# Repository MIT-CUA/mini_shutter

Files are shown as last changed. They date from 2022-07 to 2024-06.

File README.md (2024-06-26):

# mini_shutter and camera_shutter

## mini_shutter

Mini optical shutter using 4mm coreless DC motor and RP2040 driver using CircuitPython.  Allows a computer to control an optical shutter via a USB-C connection.

Mini-shutter in action

Mini-shutter2 in action

Uses a Waveshare <a
href="https://www.waveshare.com/rp2040-zero.htm">RP2040-Zero board</a>
and <a
href="https://learn.adafruit.com/welcome-to-circuitpython/what-is-circuitpython">Adafruit's
CircuitPython</a>.

Motor is an 0408 vibration motor, body diameter 4mm rated 3V, e.g. <a href="https://www.amazon.com/gp/product/B07PJDSRC7">this one from amazon</a>.

### Setup

Mini-shutter driver schematic:

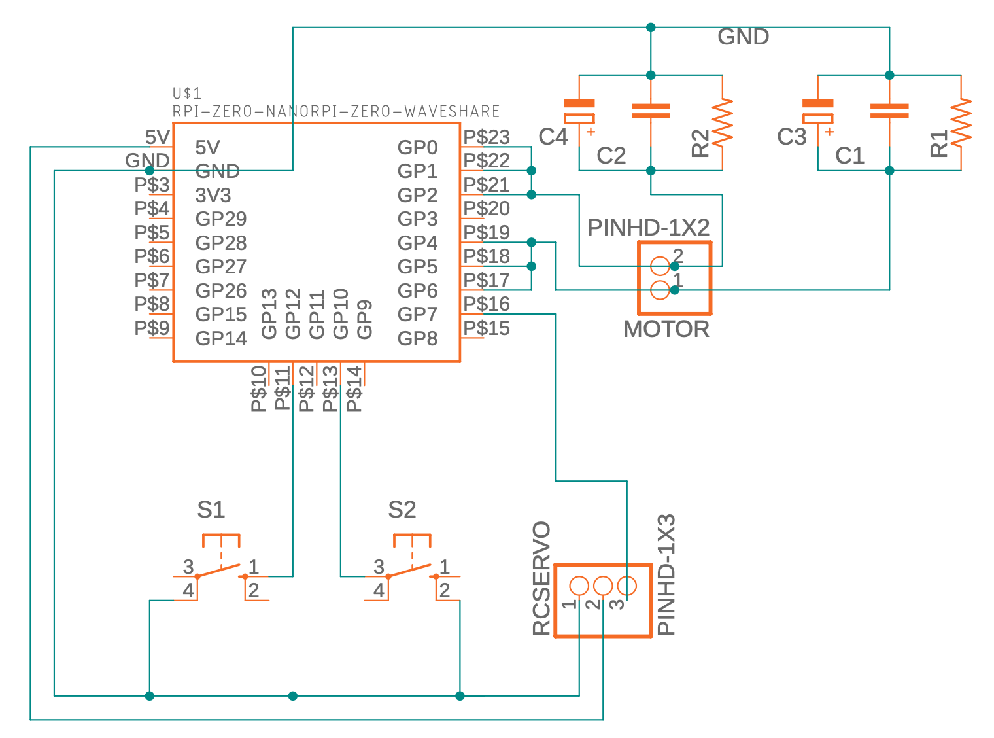
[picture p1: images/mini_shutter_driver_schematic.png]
mini-shutter driver schematic


Note that the resistors and capacitors are optional, and the header for an optional RC servo is not used.

### Loading code

1. Copy adafruit-circuitpython-raspberry_pi_pico-en_US-7.2.5.uf2 to the boot RPI-RP2 drive
2. Wait for RP2040 to re-mount itself as CIRCUITPY
3. Copy my-circuitpy-lib/* to CIRCUITPY/lib/
4. Copy mini_shutter2.py to CIRCUITPY/code.py

## camera_shutter

Camera optical shutter using DC rotating electromagnet digital camera shutter from ebay, e.g. <a href="https://www.ebay.com/itm/124456754185">this one</a>.

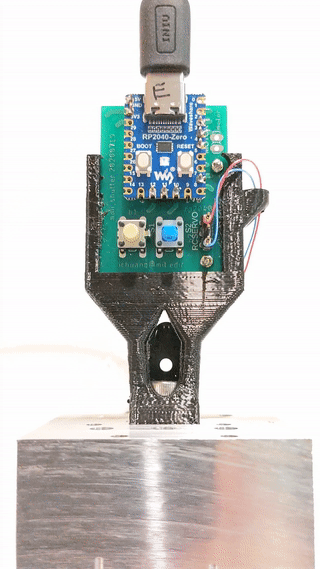
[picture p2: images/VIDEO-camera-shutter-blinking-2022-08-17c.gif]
Camera-shutter in action


Note that this shutter is normally closed, and requires a voltage to open.  The shutter springs back closed by itself when the voltage is removed.

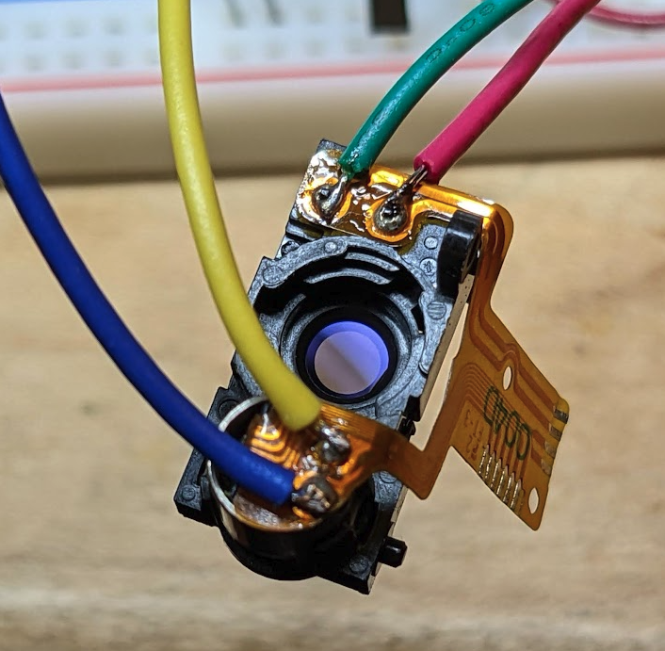
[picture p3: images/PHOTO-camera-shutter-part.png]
camera shutter part


Also, the camera shutter module has another solenoid which moves some kind of filter (or polarizer) into (and out of) the beam path, when energized (or energized in the reverse direction).

## code

See [camera_shutter.py](camera_shutter.py). New code in [main.py](ndsp/main.py), [shutter.py](ndsp/shutter.py), [photodiode.py](ndsp/photodiode.py), and [boot.py](ndsp/boot.py).

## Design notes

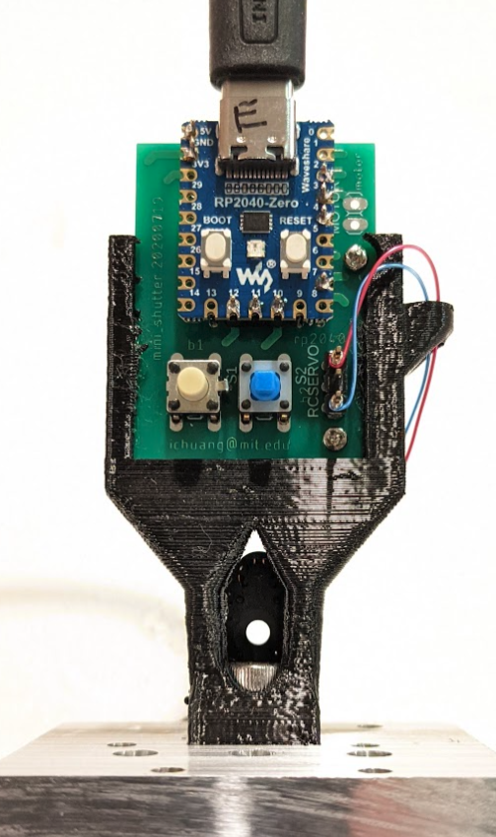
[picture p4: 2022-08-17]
images/PHOTO-camera-shutter-rp2040.png

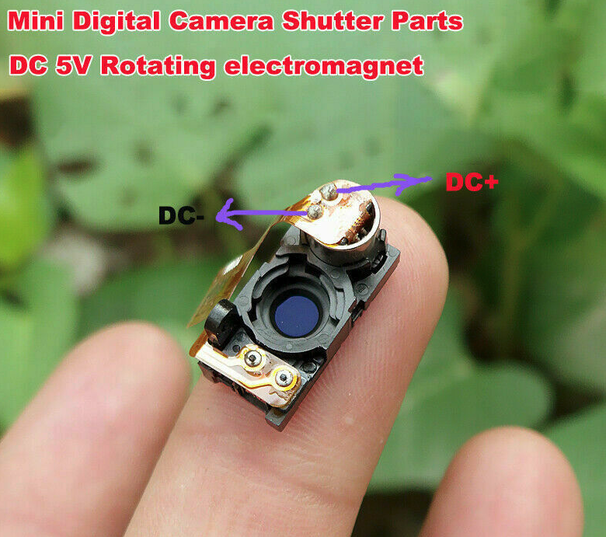
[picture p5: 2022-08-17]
images/IMAGE-digital-camera-shutter-micro-rotating-electromagnet-from-ebay-2022-08-07.png

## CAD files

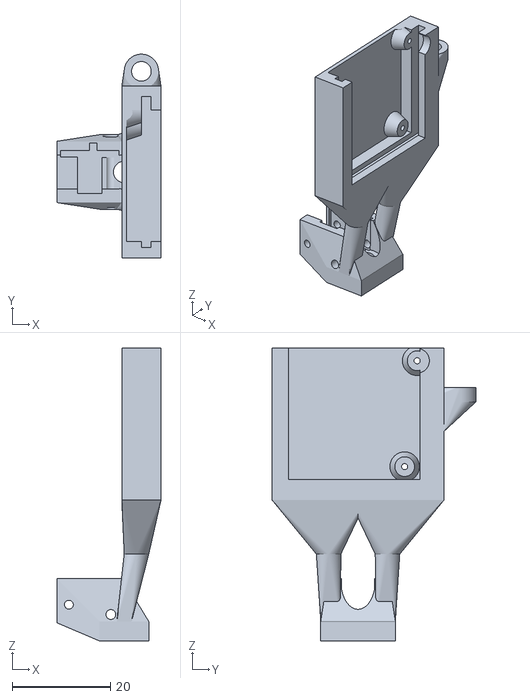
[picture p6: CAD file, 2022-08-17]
camera_shutter_mount_with_elec.stl
21.2 x 41.5 x 59.7

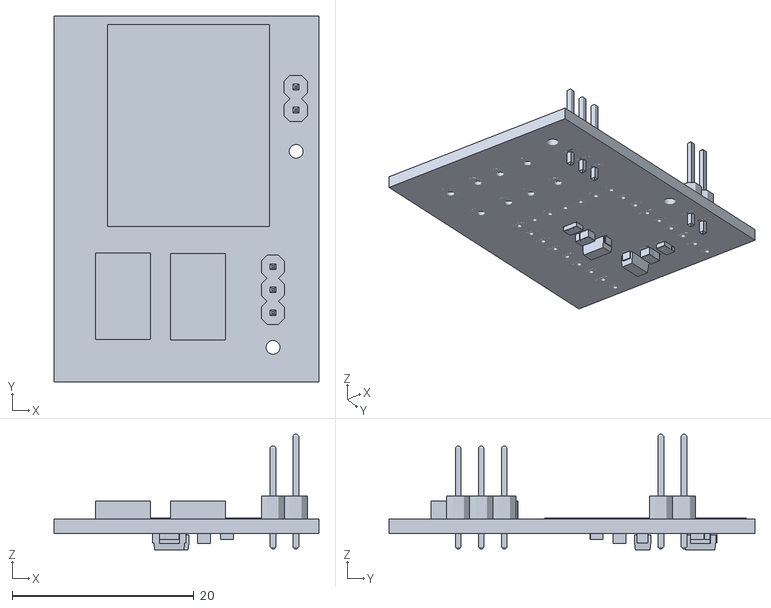
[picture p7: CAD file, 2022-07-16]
electronics/mini_shutter_driver v1.stl
29.2 x 40.3 x 12.7

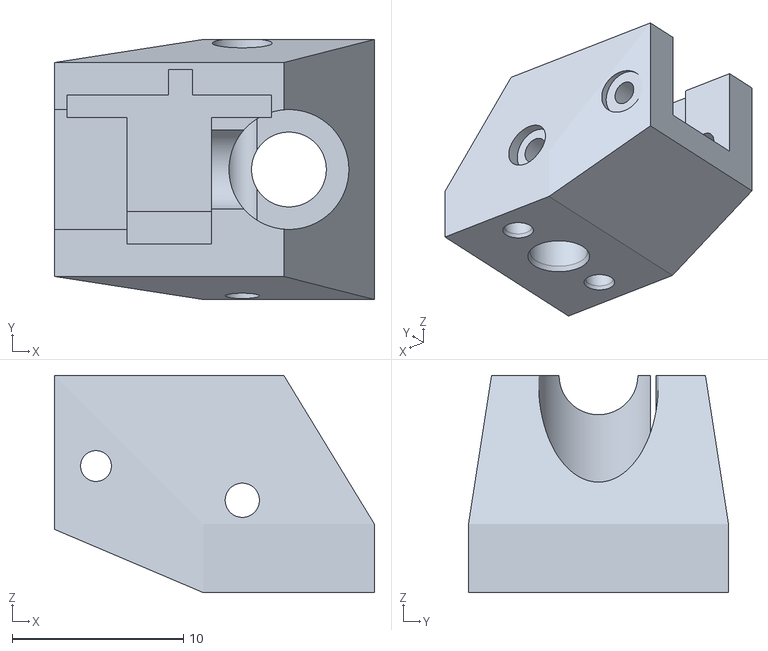
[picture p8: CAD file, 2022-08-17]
camera_shutter_mount.stl
18.7 x 15.2 x 12.7

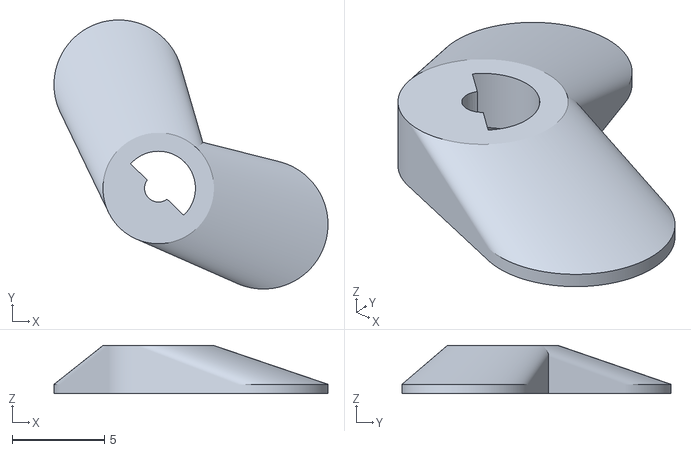
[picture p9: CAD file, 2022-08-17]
mini_shutter_blade_balanced.stl
14.8 x 14.6 x 2.60

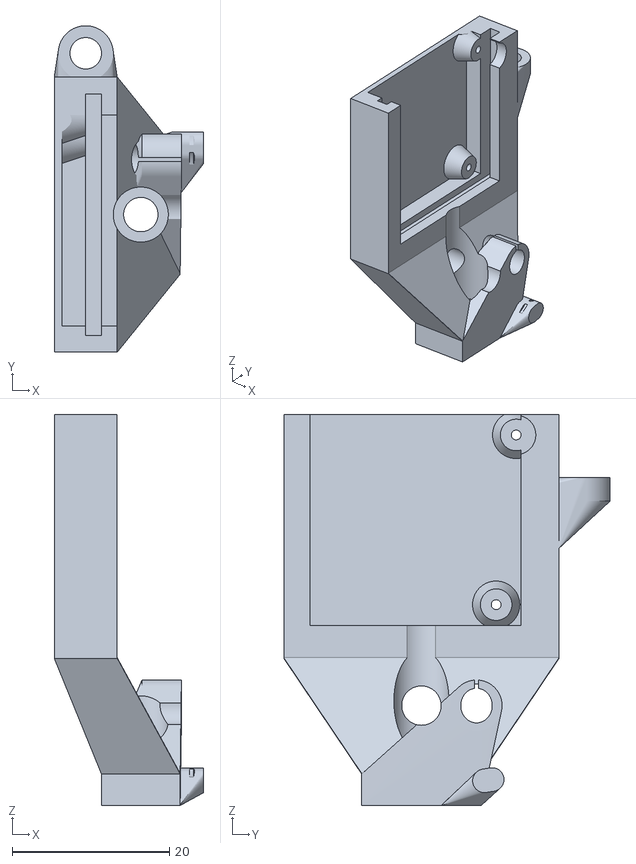
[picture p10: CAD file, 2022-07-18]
mini_shutter_mount.stl
19.0 x 41.5 x 49.7

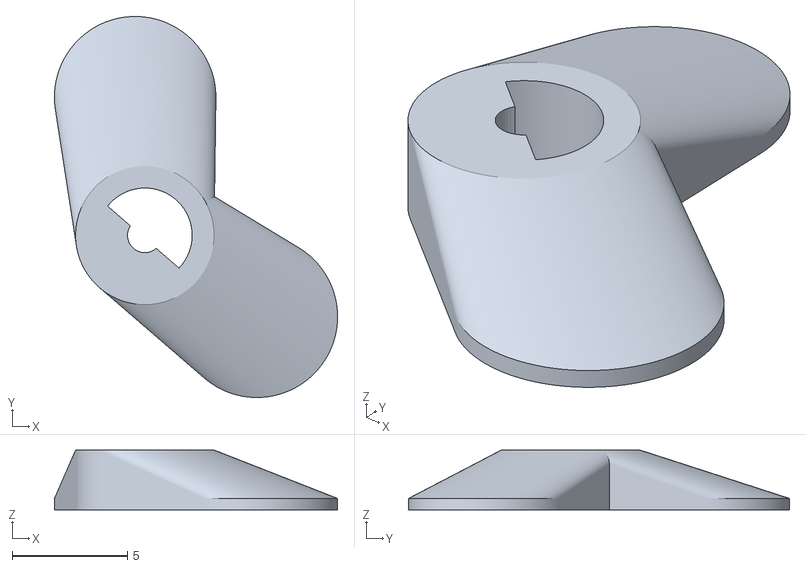
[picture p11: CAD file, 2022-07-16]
mini_shutter_blade.stl
12.3 x 16.5 x 2.60

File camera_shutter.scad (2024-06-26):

//
// camera shutter used as an optical shutter
//

//-----------------------------------------------------------------------------
// global constants

use<util.scad>;

d_inch = 25.4;
pi = 3.14159;

$fa = 0.5; // default minimum facet angle is now 0.5
$fs = 0.1; // default minimum facet size is now 0.5 mm

screw_clear_dia_4_40 = 0.120 * d_inch;
screw_tap_dia_4_40 = 0.089 * d_inch;
screw_nut_dia_4_40 = 6.4;
screw_head_clear_dia_4_40 = 5.50; // actually, pan screw head

screw_clear_dia_6_32 = 0.1450 * d_inch;
screw_tap_dia_6_32 = 0.1065 * d_inch;
screw_nut_dia_6_32 = 7.9;

screw_clear_dia_8_32 = 0.172 * d_inch;
screw_tap_dia_8_32 = 0.1360 * d_inch;
screw_nut_dia_8_32 = 8.7;           // measured from flat to flat
screw_head_clear_dia_8_32 = 7.00;   // hex
screw_washer_clear_dia_8_32 = 9.70; // thorlabs 8-32 kit washer
screw_self_tap_dia_8_32 = screw_tap_dia_8_32 + 0.5; // self-tapping for 8-32

pcb_global_z_offset = -5.0;

//-----------------------------------------------------------------------------
// camera shutter model

module cots_dc5v_camera_shutter(show = true, drill = false) {
    //
    // Uses "DC 5V Digital Camera Shutter Micro Rotating electromagnet Control
    // Switch" from ebay:
    // https://www.ebay.com/itm/124456754185?hash=item1cfa335c09:g:8tIAAOSwq4Nh7qDp
    //
    // oriented with shutter in yz plane, optical axis along x, magnet housing
    // pointing to +x and sitting above shutter.
    //
    // origin in middle of aperture
    //
    cs_dy = 8.5 + (drill ? 0.2 : 0);
    cs_dz = 17.9;
    cs_magnet_dx = 8.6;
    cs_magnet_zoff = 15.5;
    cs_magnet_dia = 6.2;
    cs_bot_stub_dy = 1.5 + (drill ? 0.4 : 0);
    cs_bot_stub_dz = 0.7 + (drill ? 0.2 : 0);
    cs_bot_dx = 4.65; // includes leads to electromagnet on bottom
    cs_dx = 4.75;     // midpoint including funnel to aperture
    // cs_aperture_dia = 6.36;
    cs_aperture_dia = 4.5;
    cs_aperture_zpos = 8.8; // distance from bottom (above stub)
    cs_bot_strut_hole_dia = 1.5 + (drill ? 0.5 : 0);
    cs_bot_strut_dx = 3.4;                      // length from back surface
    cs_bot_strut_dy = 1.2 + (drill ? 0.17 : 0); // thickness
    cs_bot_strut_dz = 3.0;
    cs_bot_strut_hole_zpos = (cs_bot_strut_dz - cs_bot_strut_hole_dia) / 2 +
                             cs_bot_strut_hole_dia / 2;
    cs_bot_strut_hole_xpos =
        -cs_dx / 2 - cs_bot_strut_dx + cs_bot_strut_hole_zpos;

    bot_pin_dz = 1.2;
    bot_pin_dx = 1.2 + (drill ? 0.3 : 0);
    bot_pin_dy = 1.5 + (drill ? 0.1 : 0);
    bot_pin_zoff = 2.8 - bot_pin_dz;
    bot_pin_xoff = 2.3 - bot_pin_dx + (drill ? 0.15 : 0);

    up_strut_dx = 3.4;
    up_strut_dy = 1.2 + (drill ? 0.1 : 0);
    up_strut_dz = 3.0;
    up_strut_hole_dia = 1.5 + (drill ? 0.3 : 0);
    up_strut_zpos = 5 - up_strut_dz;
    up_strut_hole_zpos = up_strut_zpos + up_strut_dz / 2;
    up_strut_hole_xpos = cs_dx / 2 + up_strut_dx - up_strut_dz / 2;

    cut_bot_strut_dx = cs_bot_strut_dx + (drill ? 0.2 : 0);
    cut_up_strut_dx = up_strut_dx + (drill ? 0.2 : 0);

    screw_clear_head_dia_1_7mm = 3.1 + 0.4; // head diameter for 1.7mm screw

    bot_mag_cut_dx = 20;
    bot_mag_cut_dz = 20;
    bot_mag_cut_dy = 7;
    bot_mag_cut_zoff = 2;

    bot_front_cut_dx = 6;

    module holes() {
        screw_head_yoff = cs_dy / 2 + 2;
        color("red") {
            translate([ 0, 0, cs_aperture_zpos ]) rotate([ 0, 90, 0 ])
                translate([ 0, 0, -10 ])
                    cylinder(d = cs_aperture_dia,
                             h = 20); // main aperture for optical beam path
            translate([ cs_bot_strut_hole_xpos, 0, cs_bot_strut_hole_zpos ]) {
                rotate([ 90, 0, 0 ]) {
                    translate([ 0, 0, -10 ]) cylinder(
                        d = cs_bot_strut_hole_dia, h = 20); // bottom strut hole
                    translate([ 0, 0, screw_head_yoff ]) cylinder(
                        d = screw_clear_head_dia_1_7mm, h = 20); // screw head
                }
            }
            translate([ up_strut_hole_xpos, 0, up_strut_hole_zpos ]) {
                rotate([ 90, 0, 0 ]) {
                    translate([ 0, 0, -10 ]) cylinder(d = up_strut_hole_dia,
                                                      h = 20); // up strut hole
                    translate([ 0, 0, screw_head_yoff ]) cylinder(
                        d = screw_clear_head_dia_1_7mm, h = 20); // screw head
                }
            }
        }
    }

    translate([ 0, 0, -cs_aperture_zpos ]) {
        difference() {
            union() {
                cut_dx = cs_dx + (drill ? 0.2 : 0);
                color("silver") translate([ -cut_dx / 2, -cs_dy / 2, 0 ])
                    cube([ cut_dx, cs_dy, cs_dz ]);
                color("gray") translate([
                    -cut_dx / 2, -cs_bot_stub_dy + cs_dy / 2,
                    -cs_bot_stub_dz + 0.01
                ]) // stub on bottom right
                    cube([ cut_dx, cs_bot_stub_dy, cs_bot_stub_dz ]);
                color("black") translate([
                    -cut_bot_strut_dx - cs_dx / 2, -cs_dy / 2, 0
                ]) // strut bottom left back
                    cube(
                        [ cut_bot_strut_dx, cs_bot_strut_dy, cs_bot_strut_dz ]);
                color("black") translate([
                    cs_dx / 2, -cs_dy / 2,
                    up_strut_zpos
                ]) // strut upper left front
                    cube([ cut_up_strut_dx, up_strut_dy, up_strut_dz ]);
                color("black") translate([
                    -cs_dx / 2 + bot_pin_xoff, -cs_dy / 2 - bot_pin_dy,
                    bot_pin_zoff
                ]) // bottom pin
                    cube([ bot_pin_dx, bot_pin_dy, bot_pin_dz ]);
                color("green") translate(
                    [ -cs_dx / 2, 0, cs_magnet_zoff ]) // magnet cylinder
                    rotate([ 0, 90, 0 ])
                        cylinder(d = cs_magnet_dia, h = cs_magnet_dx);
            }
            holes();
        }
        if (drill) {
            color("pink") {
                translate([ cs_dx / 2, -cs_dy / 2, 0 ]) // slot for up strut
                    cube([ cut_up_strut_dx, up_strut_dy, up_strut_zpos + 14 ]);
                translate([
                    -cut_bot_strut_dx - cs_dx / 2, -cs_dy / 2, 0
                ]) // slot for bot strut
                    cube([
                        cut_bot_strut_dx, cs_bot_strut_dy, cs_bot_strut_dz + 10
                    ]);
                translate([
                    -cs_dx / 2 + bot_pin_xoff, -cs_dy / 2 - bot_pin_dy + 0.01, 0
                ]) // bottom pin
                    cube([ bot_pin_dx, bot_pin_dy, 16 ]);
                translate([
                    -cs_dx / 2, -bot_mag_cut_dy / 2,
                    bot_mag_cut_zoff
                ]) // cutout to access bottom magnet pins
                    cube([ bot_mag_cut_dx, bot_mag_cut_dy, bot_mag_cut_dz ]);
                translate([
                    -bot_front_cut_dx, -bot_mag_cut_dy / 2,
                    bot_mag_cut_zoff
                ]) // cutout for bottom front
                    cube([ bot_front_cut_dx, bot_mag_cut_dy, bot_mag_cut_dz ]);
            }
            holes();
        }
    }
}

// -----------------------------------------------------------------------------
// c05g mount onto baseplate

module baseplate_mount_holes(slen = 5) {
    //
    // holes for mounting onto baseplate: 8-32 screw and two 2mm pins,
    // compatible with footprint of thorlabs c05 polaris mirror mount.
    //
    // slen = screw length (dz before screw head)
    //
    pin_dia = 2.0;
    pin_dy = 5.0;
    pin_dz = 2.2;
    cylinder(d = screw_clear_dia_8_32, h = 20 - 6);
    translate([ 0, 0, slen ]) {
        cylinder(d = screw_head_clear_dia_8_32, h = 20 - 8);
    }
    translate([ 0, 0, -0.01 ])
        cylinder(d1 = screw_clear_dia_8_32 + 0.4, d2 = screw_clear_dia_8_32,
                 h = 0.5); // taper to compensate for print bed lip
    for (dy = [ -1, 1 ]) {
        translate([ 0, dy * pin_dy, 0 ]) {
            cylinder(d = pin_dia + 0.1, h = pin_dz);
            translate([ 0, 0, -0.01 ])
                cylinder(d1 = pin_dia + 0.4, d2 = pin_dia + 0.1,
                         h = 0.4); // taper to compensate for print bed lip
        }
    }
}

// -----------------------------------------------------------------------------
// controller electronics

module controller_pcb(show = true, drill = false, holes = false) {
    // PCB in XY plane with origin on bottom side at y-midpoint along board edge
    // pointing along -x direction
    pcb_dx = 29.2;
    pcb_dy = 40.35;
    pcb_thick = 2;

    mount_screw_dia = 1.25;
    mount_screw_head_dia = 5;

    if (show) {
        rotate([ 0, 0, 90 ]) translate([ -pcb_dx / 2, -pcb_dy * 0, 0 ])
            import("electronics/mini_shutter_driver v1.stl");
    }
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

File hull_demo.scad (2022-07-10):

// illustrate use of hull() for connecting parts

$fa=0.5; // default minimum facet angle is now 0.5
$fs=0.1; // default minimum facet size is now 0.1 mm

module first(){
     color("orange") cube([10, 10, 4]);
     color("blue") translate([0, 0, 8]) rotate([0, 90, 0])
	  cylinder(d=4, h=8);
}

module second(){
     color("orange"){

	  hull(){
	       cube([10, 10, 4]);
	       translate([0, 0, 8]) rotate([0, 90, 0])
		    cylinder(d=4, h=8);
	  }

     }
}

module third(){
     color("blue")
	  translate([0, 0, 8]) rotate([0, 90, 0]) cylinder(d=3, h=12);
     color("orange"){
	  hull(){
	       cube([10, 10, 4]);
	       translate([2, 0, 8]) rotate([0, 90, 0])
		    cylinder(d=4, h=4);
	  }
     }
}

// first();
second();
// third();

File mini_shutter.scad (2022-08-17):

//
// mini optical shutter for baseplate (1/2" beam height) using
// 4mm diameter coreless DC motor.
//
// motor is easily driven by current from digital output pin
// of RP2040 microcontroller

//-----------------------------------------------------------------------------
// global constants

use <util.scad>;

d_inch = 25.4;
pi = 3.14159;

$fa=0.5; // default minimum facet angle is now 0.5
$fs=0.1; // default minimum facet size is now 0.5 mm

screw_clear_dia_4_40 = 0.120 * d_inch;
screw_tap_dia_4_40   = 0.089 * d_inch;
screw_nut_dia_4_40   = 6.4;
screw_head_clear_dia_4_40 = 5.50;	// actually, pan screw head

screw_clear_dia_6_32 = 0.1450 * d_inch;
screw_tap_dia_6_32   = 0.1065 * d_inch;
screw_nut_dia_6_32   = 7.9;

screw_clear_dia_8_32 = 0.172 * d_inch;
screw_tap_dia_8_32   = 0.1360 * d_inch;
screw_nut_dia_8_32   = 8.7;		// measured from flat to flat
screw_head_clear_dia_8_32 = 7.00;	// hex
screw_washer_clear_dia_8_32 = 9.70;	// thorlabs 8-32 kit washer
screw_self_tap_dia_8_32 = screw_tap_dia_8_32 + 0.5;		// self-tapping for 8-32

// -----------------------------------------------------------------------------
// options


// -----------------------------------------------------------------------------
// mini 4mm coreless dc motor

module motor_4mm_coreless_dc(show=true, drill=false, theta=-45, drill_slot=true, mount_dia_extra=0){
     //
     // motor pointing up towards +z, positioned with bottom of cam
     // (closest side of cam to motor) at origin.  shaft has a cam on it.
     //
     // theta = angle of motor cam
     // drill_slot = include slot for motor housing clamp
     // 
     body_dz = 8.2;
     shaft_dia = 0.75;
     cam_outer_dia = 4.0;
     cam_dz = 2.5;
     cam_shaft_dia = 1.5;
     cam_yoff = -0.1;
     oal = 11.4;				// overall length
     slot_dy = 0.5;
     slot_dx = 8;
     module cam(show=true, drill=false){
	  color("blue"){
	       acod = cam_outer_dia + (drill ? 0.9 - 0.9 : 0);
	       rotate([-50, 0, 0])
		    translate([-acod/2, -0.4 + cam_yoff, -0.3]){	// compensate for print burr - flat side
			 color("red") cube([acod, 0.5, 0.7]);
		    }
	       cylinder(d=cam_shaft_dia, h=cam_dz + (drill ? 1 : 0) );	// cam center - on shaft
	       cylinder(d1=cam_shaft_dia + (drill ? 0.9 + 0.4 : 0), d2=cam_shaft_dia, h=0.6 );	// cam center - on shaft - compensate for print plate burr
	       difference(){
		    union(){
			 cylinder(d1=cam_outer_dia + (drill ? 0.9 + 0.2 : 0),	// compensate for burr on print plate
				  d2=cam_outer_dia + (drill ? 0.0 : 0),
				  h=0.6);
			 cylinder(d=cam_outer_dia + (drill ? 0.0 : 0),
				  h=cam_dz + (drill ? 1 : 0));
		    }
		    translate([-5, -10 + cam_yoff, -1]){
			 color("red") cube([10, 10, 10]);
		    }
	       }
	  }
     }
     union(){
	  extra_dz = (drill ? 8 : 0);		// extra tube length when drilling, for wires to exit
	  extra_dia = mount_dia_extra;		// possibly different diameter when drilling, so motor fits snugly in motor housing
	  translate([0, 0, -oal + cam_dz]){
	       translate([0, 0, -extra_dz]) color("silver"){
		    scale([1 + (drill ? 0.1 : 0), 1, 1])	// for holder, compensate for underhang from top when printing
			 cylinder(d=4 + extra_dia, h=body_dz + extra_dz);	// main cylindrical body of motor
		    if (drill && drill_slot){
			 // cut slot along side of motor, so the motor housing can hold motor with natural spring clamp action
			 translate([-slot_dx, -slot_dy/2, 0])
			      cube([slot_dx, slot_dy, body_dz + extra_dz]);
		    }
	       }
	       translate([0, 0, 0.01]) color("black") cylinder(d=cam_shaft_dia, h=oal-0.01);	// motor shaft
	  }
	  rotate([0, 0, theta])
	       cam(show=show, drill=drill);		// cam at end of shaft
     }
}

// -----------------------------------------------------------------------------
// c05g mount onto baseplate

module baseplate_mount_holes(slen=5){
     //
     // holes for mounting onto baseplate: 8-32 screw and two 2mm pins,
     // compatible with footprint of thorlabs c05 polaris mirror mount.
     //
     // slen = screw length (dz before screw head)
     //
     pin_dia = 2.0;
     pin_dy = 5.0;
     pin_dz = 2.2;
     cylinder(d=screw_clear_dia_8_32, h=20);
     translate([0, 0, slen]){
	  cylinder(d=screw_head_clear_dia_8_32, h=20);
     }
     translate([0, 0, -0.01])
	  cylinder(d1=screw_clear_dia_8_32 + 0.4, d2=screw_clear_dia_8_32, h=0.5);	// taper to compensate for print bed lip
     for(dy=[-1,1]){
	  translate([0, dy*pin_dy, 0]){
	       cylinder(d=pin_dia+0.1, h=pin_dz);
	       translate([0, 0, -0.01])
		    cylinder(d1=pin_dia + 0.4, d2=pin_dia + 0.1, h=0.4);	// taper to compensate for print bed lip
	  }
     }
}

// -----------------------------------------------------------------------------
// controller electronics

module controller_pcb(show=true, drill=false, holes=false){
     // PCB in XY plane with origin on bottom side at y-midpoint along board edge
     // pointing along -x direction
     pcb_dx = 29.2;
     pcb_dy = 40.35;
     pcb_thick = 2;

     mount_screw_dia = 1.25;
     mount_screw_head_dia = 5;

     if (show){
	  rotate([0, 0, 90])
	       translate([-pcb_dx/2, -pcb_dy*0, 0])
	       import("electronics/mini_shutter_driver v1.stl");
     }

     module mounting_holes(zoff=0){
	  for(xy=[ [-3.83, 9.5], [-25.4, 9.5+2.54] ]){
	       translate([xy[0], xy[1], zoff])
		    children();
	       }
     }

     if (drill){
	  if (1){
	       slot_width = pcb_dx + 1.5;
	       translate([ -pcb_dy, -slot_width/2, 0]){
		    color("pink"){
			 cube([pcb_dy, slot_width, pcb_thick]);			// PCB
		    }
		    color("orange"){					// components on PCB
			 rim = 1.2;
			 comp_thick = 7;
			 translate([-rim, rim, -0.01])
			      cube([pcb_dy, pcb_dx-2*rim, comp_thick]);		// top-side components
		    }
		    difference(){
			 color("brown"){					// bottom-side components on PCB
			      rim = 1.2;
			      comp_thick = 3;
			      translate([-rim, rim, -comp_thick])
				   cube([pcb_dy, pcb_dx-2*rim, comp_thick]);		// bottom-side components
			 }
			 color("red"){
			      translate([ pcb_dy, slot_width/2, -3]){
				   mounting_holes(){
					cylinder(d1=6, d2=4, h=3);		// feet for mounting screws
				   }
			      }
			 }
		    }
	       }
	  }
	  color("red"){
	       mounting_holes(zoff=-10)
		    cylinder(d=mount_screw_dia, h=20);		// screw holes
	       mounting_holes(zoff=0)
		    cylinder(d=mount_screw_head_dia, h=20);		// screw head holes
	  }
     }

     if (holes){
	  mounting_holes();
     }
}

module electronics_mount(show=true, show_bottom=false, show_electronics=false){
     //
     // mount for control electronics PCB, oriented in lab frame (of final optical shutter).
     // holds PCB from outer rim, to allow space for components (on both sides of PCB),
     // including the RP2040 module.
     // Open at top for USB-C connector
     // Open at front for push-buttons
     //
     // if show_bottom then make rectangle for bottom of mount (for hull to something else)
     //
     mount_dy = 35;
     mount_dx = 8;
     mount_dz = 40 - 9;
     mount_xoff = -2;
     pcb_zoff = 3;

     module epos(){
	  translate([0, 0, pcb_zoff])
	       rotate([0, 90, 0])
	       children();
     }

     module bottom(){
	  translate([-mount_dx/2, -mount_dy/2, 0])
	       cube([mount_dx, mount_dy, 0.1]);
     }

     if (show){
	  difference(){
	       sr_zoff = 24 - 4;	// strain relief z-offset
	       sr_yoff = 3;
	       sr_od = mount_dx-1;
	       sr_id = 4;
	       sr_dz = 3;
	       union(){
		    translate([-mount_dx/2, -mount_dy/2, 0])
			 color("blue")
			 cube([mount_dx, mount_dy, mount_dz]);
		    difference(){
			 hull(){
			      translate([0, mount_dy/2 + sr_yoff, sr_zoff])
				   cylinder(d=sr_od, h=sr_dz);
			      translate([0, 0, sr_zoff-sr_dz - 3])
				   bottom();
			 }
			 translate([0, mount_dy/2 + sr_yoff, sr_zoff-10])
			      color("red")
			      cylinder(d=sr_id, h=20);
		    }
	       }
	       epos()
		    controller_pcb(show=false, drill=true);
	  }
     }
     if (show_bottom){
	  bottom();
     }
     if (show_electronics){
	  epos()
	       controller_pcb(show=true, drill=false);
     }
}

// -----------------------------------------------------------------------------
// shutter with mount
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

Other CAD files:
util.scad

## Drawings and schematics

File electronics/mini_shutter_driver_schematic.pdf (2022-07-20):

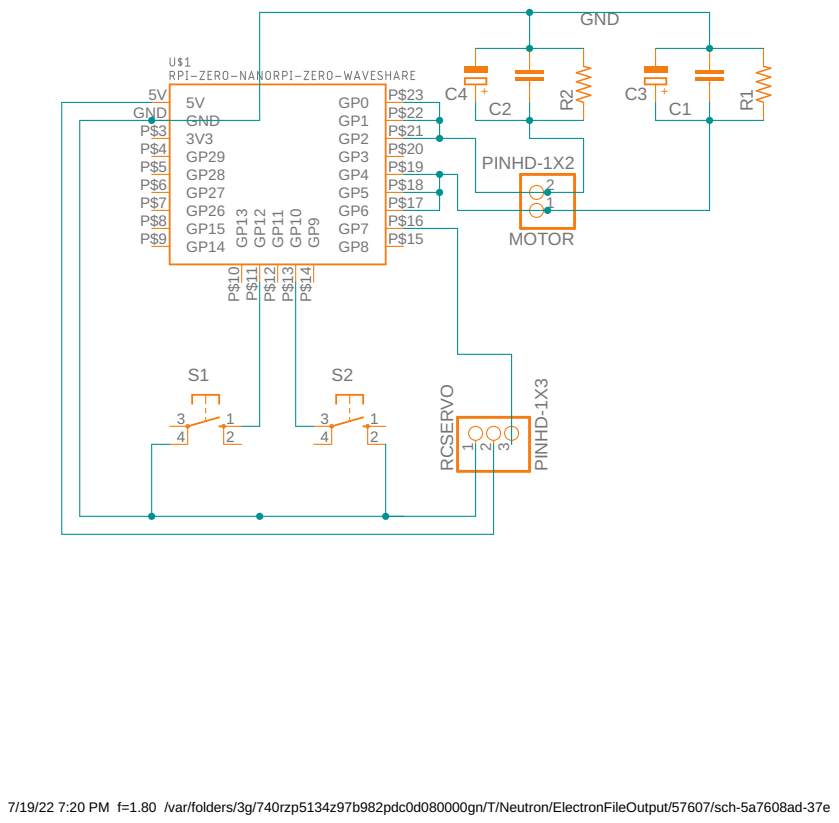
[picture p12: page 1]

7/19/22 7:20 PM f=1.80 /var/folders/3g/740rzp5134z97b982pdc0d080000gn/T/Neutron/ElectronFileOutput/57607/sch-5a7608ad-37e2-4f54-81ba-9fdea8c5b5c8/Untitled.sch (Sheet: 1/1)

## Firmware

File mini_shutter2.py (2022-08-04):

#
# mini_shutter2.py: run 4mm coreless DC motor (used for an optical shutter)
# either back and forth - opening and closing repeatedly
# or button pushes to open & close
#

import time
import board
import pwmio
import usb_hid
import neopixel
import supervisor
from digitalio import DigitalInOut, Direction, Pull
from adafruit_debouncer import Debouncer

# BUTTON_PIN = board.GP27
BUTTON_PIN = board.GP12
the_button = DigitalInOut(BUTTON_PIN)		# button digital input
the_button.direction = Direction.INPUT
the_button.pull = Pull.UP

# BUTTON_PIN2 = board.GP15
BUTTON_PIN2 = board.GP10
the_button2 = DigitalInOut(BUTTON_PIN2)		# button digital input
the_button2.direction = Direction.INPUT
the_button2.pull = Pull.UP

# motor_open = DigitalInOut(board.GP7)
# motor_close = DigitalInOut(board.GP6)

motor_open_pins  = [ board.GP0, board.GP1, board.GP2 ]
motor_close_pins = [ board.GP4, board.GP5, board.GP6 ]
motor_open  = [ pwmio.PWMOut(m, frequency=500, duty_cycle=0) for m in motor_open_pins ]
motor_close = [ pwmio.PWMOut(m, frequency=500, duty_cycle=0) for m in motor_close_pins ]

sw1 = Debouncer(the_button)
sw2 = Debouncer(the_button2)

led = neopixel.NeoPixel(board.GP16, 1)
led.brightness = 0.3

print("mini_shutter2.py")
print("(h) help")

def shutter_open():
    led[0] = (5, 0, 0)
    for m in motor_close:
        m.duty_cycle = 0
    for cycle in range(32768, 65535, 1000):
        for m in motor_open:
            m.duty_cycle = cycle
    time.sleep(0.3)
    for m in motor_open:
        # m.duty_cycle = 10000	# keep slightly powered
        m.duty_cycle = 0	# unpowered
    led[0] = (0, 0, 0)
    print("open")
    
def shutter_close():
    led[0] = (0, 5, 0)
    for m in motor_open:
        m.duty_cycle = 0
    for cycle in range(32768, 65535, 1000):
        for m in motor_close:
            m.duty_cycle = cycle
    time.sleep(0.3)
    for m in motor_close:
        m.duty_cycle = 0
    led[0] = (0, 0, 0)
    print("close")

def process_buttons():
    global mode
    sw1.update()		# button debouncing
    sw2.update()
    if not sw1.value:
        shutter_open()
        while not sw1.value:    # Wait for button to be released
            if not sw2.value:	# if both buttons pushed
                mode = "osc"
            sw1.update()
            sw2.update()
        return
        
    if not sw2.value:
        shutter_close()
        while not sw2.value:    # Wait for button to be released
            if not sw1.value:	# if both buttons pushed
                mode = ""
            sw1.update()
            sw2.update()
        return

mode = ""
opened = False
last_time = time.monotonic()

def oscillate():
    global opened, last_time
    now = time.monotonic()
    if now-last_time < 0.5:
        return
    last_time = now
    if opened:
        shutter_close()
        opened = False
    else:
        shutter_open()
        opened = True

def process_input():
    global mode
    if not supervisor.runtime.serial_bytes_available:
        return
    value = input().strip()
    if value=="r":
        print("running oscillation...")
        mode = "osc"
    elif value=="o":
        mode = ""
        shutter_open()
    elif value=="c":
        mode = ""
        shutter_close()
    elif value=="s":
        mode = ""
        print("stopped")
    elif value=="h":
        print("(o) open, (c) close, (r) run oscillate, (s) stop")

# flicker LED to indicate power-up
led[0] = (5, 0, 0)
time.sleep(0.1)
led[0] = (0, 5, 0)
time.sleep(0.1)
led[0] = (0, 0, 5)
time.sleep(0.1)
led[0] = (0, 0, 0)
shutter_open()

# main loop
while True:
    process_buttons()
    process_input()
    if mode=="osc":
        oscillate()

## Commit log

2022-07-10 mini_shutter OpenSCAD and circuitpython code
    [mini_shutter.scad, mini_shutter_blade.stl, mini_shutter_mount.stl]
2022-07-10 mini_shutter.scad - better endstop latching for closed position
    [mini_shutter.scad, mini_shutter_mount.stl]
2022-07-10 add hull_demo.scad
    [hull_demo.scad]
2022-07-15 change motor pins to match pcb
2022-07-16 mini shutter scad with mount for control electronics - also larger blade block and movement
    [mini_shutter.scad, mini_shutter_blade.stl, mini_shutter_driver v1.stl, mini_shutter_mount.stl]
2022-07-18 driver code using PWM ; scad endstop with less catch
    [mini_shutter.scad, mini_shutter_mount.stl]
2022-07-18 balanced shutter blade; smaller endstop, wider opened position
    [mini_shutter.scad, mini_shutter_blade_balanced.stl, mini_shutter_mount.stl]
2022-07-19 good working version - scad and mini_shutter2.py
    [mini_shutter.scad]
2022-08-17 mini_shutter blade balanced - more compensation for print bed burr
    [mini_shutter.scad, mini_shutter_blade_balanced.stl]
2022-08-17 camera shutter
    [camera_shutter.scad, camera_shutter_mount.stl, camera_shutter_mount_with_elec.stl]
2022-08-17 camera shutter image
2023-07-26 all updates
    [camera_shutter.scad, copper_bottom.gbr, copper_top.gbr, drill_1_16.xln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]
2023-08-04 end of week. ¯\_(ツ)_/¯
2023-08-17 comments and final calibration stuff
